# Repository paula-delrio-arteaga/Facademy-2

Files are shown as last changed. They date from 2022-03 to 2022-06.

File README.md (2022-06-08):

# Fabacademy-2
Micro challenge 2
## PHOTOBIOREACTOR

### CONCEPT

Photobioreactor hosting our algae cultures to help them grow. 

### PURPOSE

We wanted to explore the properties of algae for different individual purposes so we decided to start collaborating in the creation of the habitat for its propagation. Once we understand the species then we can be able to collaborate with them in order to develop other projects. We are interested in co-creating with algae and exploring their bioremediation abilities. After gathering enough algae we can then transform it into either food, materials, energy, biofuel, art and other individual purposes. 

### PLANNING AND EXCECUTION

We started by defining the needs of our algae and how many cultures we wanted to have. We decided to start with spirulina. We ordered the spirulina and while it arrived we started researching what we needed in order to keep it alive and help it grow. We got a manual which we are attaching in the files. From this we were able to make a list of the things we needed for cultivating the spirulina. We also reserached how the electronics would work and what parts we needed to get. After having in mind all the components neeeded then we could figure out how the design could look like. 

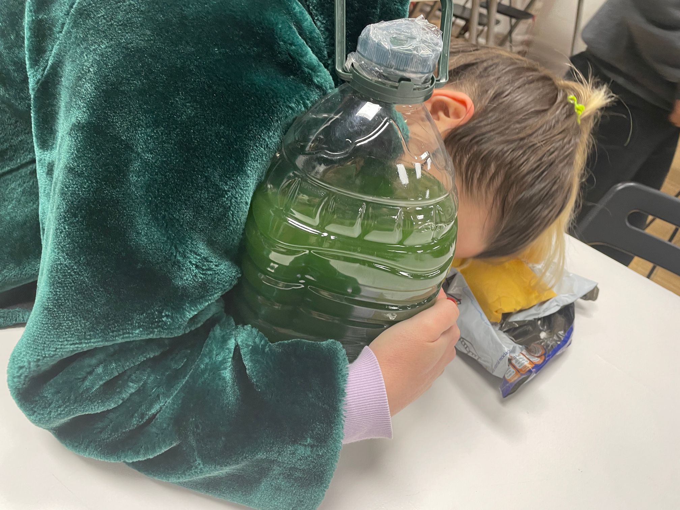
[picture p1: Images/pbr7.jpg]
spirulinalove


Now we started designing how will the spirulina be displayed and how would it work. The tricky part in this was integrating the electronics into the stand for the spirulina. Needing them to be sort of close but also protected in case of any spills.

At first we wanted to create a base box that would hold the 4 bottles of spirulina we wanted to have, one for each of us. The design was intended to have the electronics in the box with the led lights facing upwards to the spirulina. We wanted to do the box with cnc and add some curves which would be done with milling so it would add a more organic aesthethic to it. 

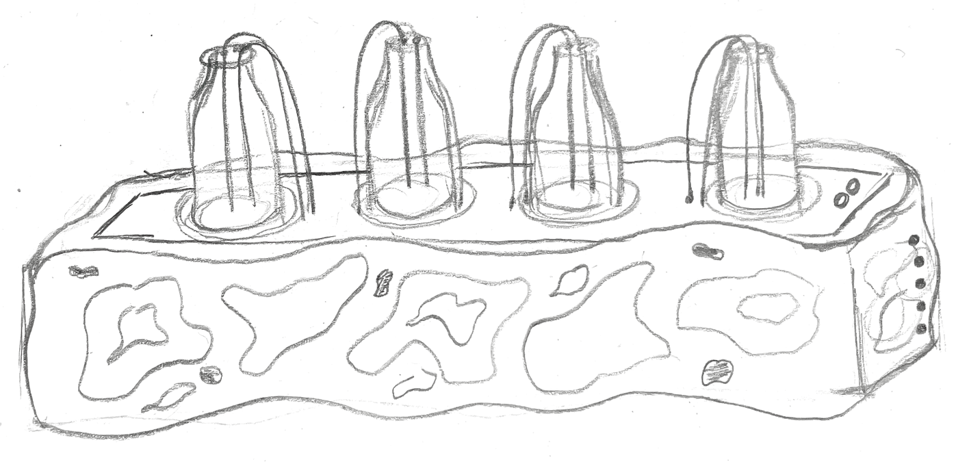
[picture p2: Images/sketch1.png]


After discussing it we realised it would take a lot of time to fabricate and we would also have a lot of kerf. After assesing this and seeing more options we decided to change the design into something that would make more sense with an organic structure around the spirulina. So we decided to test this and start sketching some ideas. When we finally agreed on a design we divided by tasks. 

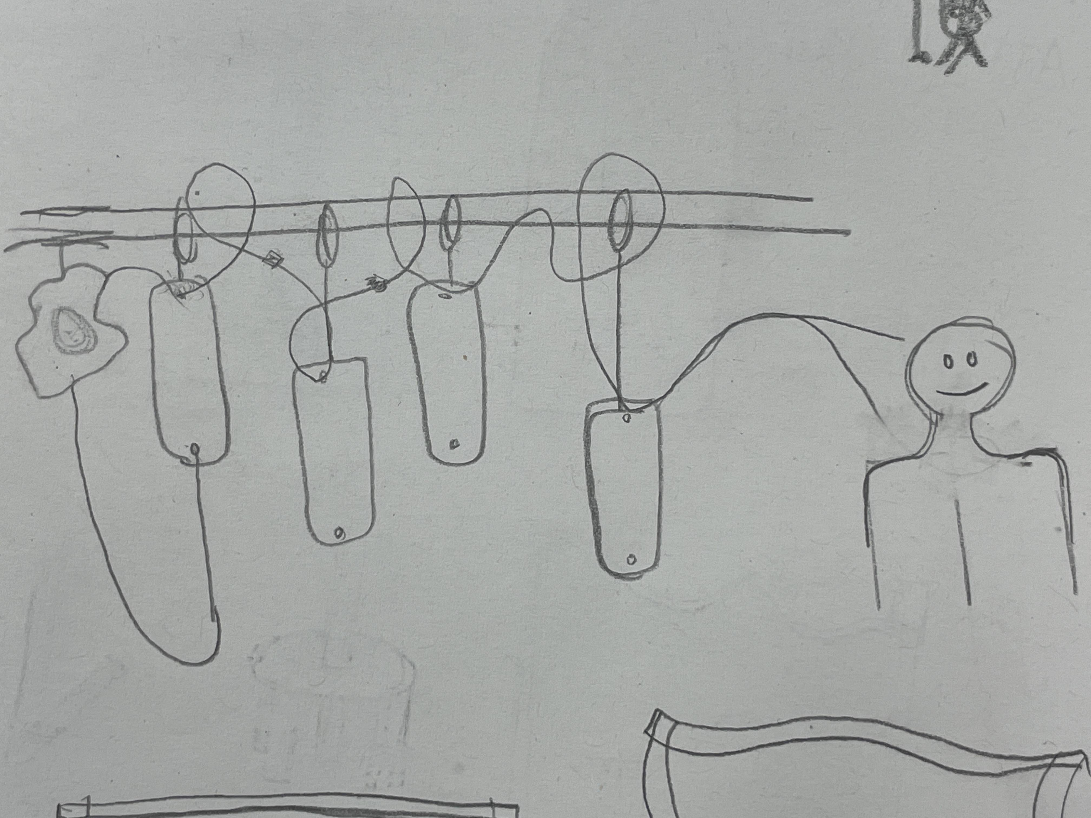
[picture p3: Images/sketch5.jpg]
sketchstand


#### CNC

  -We started making the 3D model and plans of the curves that would be fitting below the hung spirulina bottles. We 3D modelled the electronics box in which we were going to place the power, pumps, arduino and the cables. We decided to cut it in 15mm plywood. We cut 2 pieces and added a 5mm pocketing in which the LED lights would pass through, so when we glued both pieces together we could have a 1 cm rail. 
  
  -After setting up the file in rhino, we used the rhinoCam plug in and generated the code for the CNCing. We started by setting up a box which would be the material we selected and the dimensions of it. We used a board of 1200x2400x15.6 aprox. We then defined which curves would be an outer cut, inner cut and pocketing.
  
  -We also created the tool specifications, we used a Flat Mill of 6mm. We had to add the bridges in some of the pieces so they would stay in place and add the file of the screws. After defining all the settings we were ready to export the code. The screws file was exported individually and the rest of the layers were exported together. 
  
  -Once we had the nc code we went to the machine, we put out glasses, hair tie and ear cuffs on (safety first). 
  
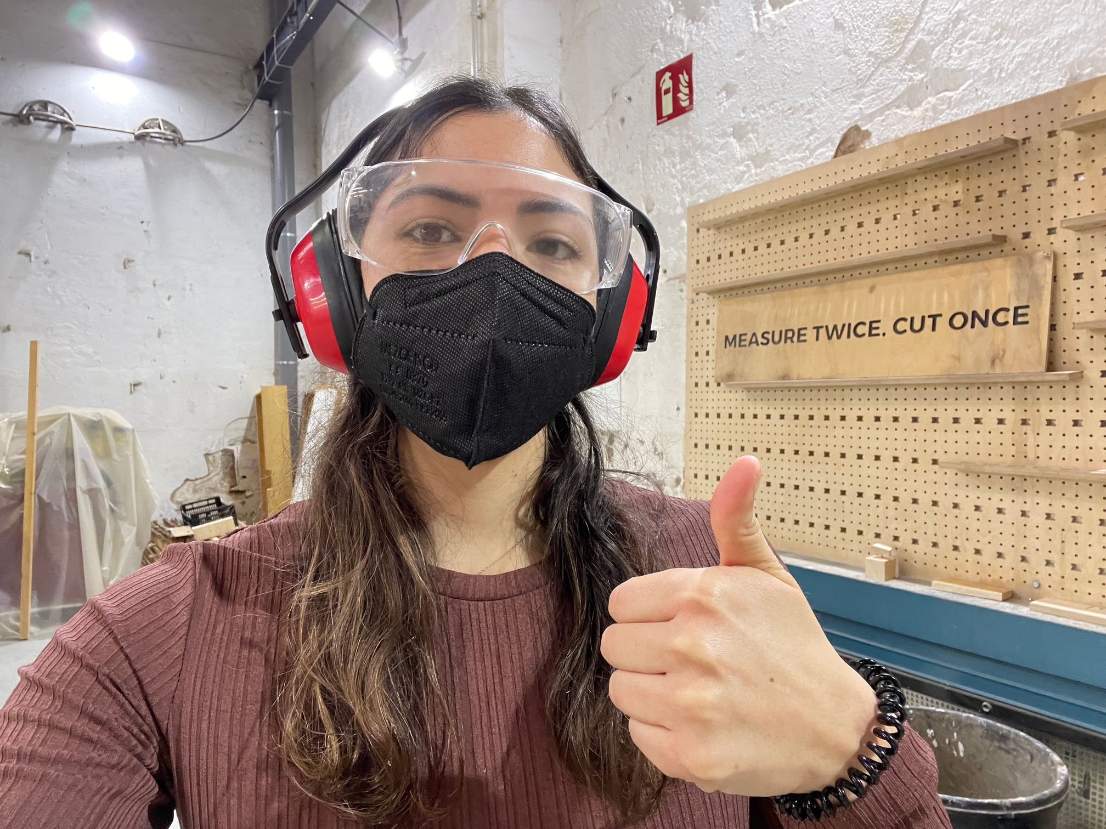
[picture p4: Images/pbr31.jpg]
safetyfirst
  
  
  -We cleaned the bed of the cnc of any extra material left from before, we placed our plywood sheet and aligned it to the borders of the bed. Then we calibrated the z axis with the button of the cnc. So we placed the button below the tip of the CNC and calibrated it. After getting that ready we opened our file in the computer and ran the screws file. 
  
  -After the marks for the screws were done we moved the head of the CNC in order to get on top and screw. 
  
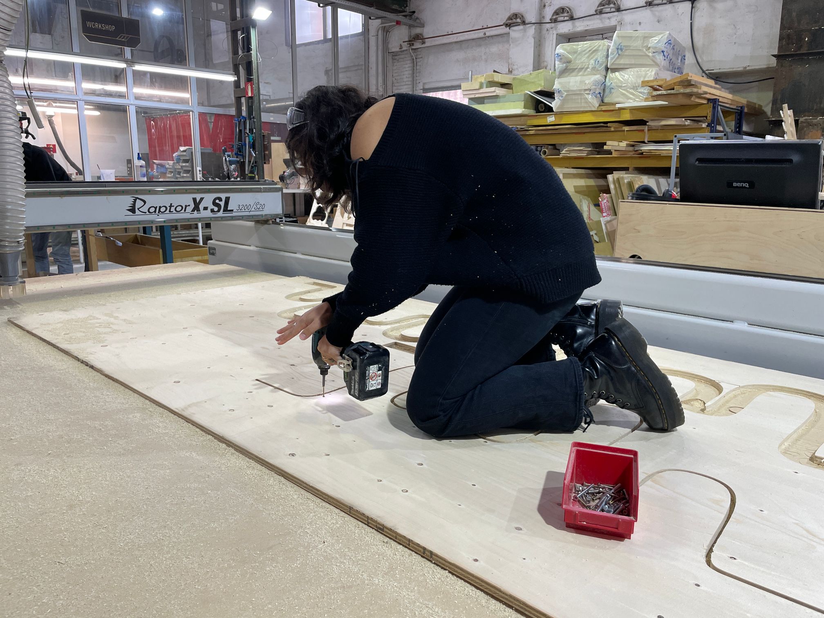
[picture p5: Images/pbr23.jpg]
screwingplywood
  
  
  -Once the material was already screwed onto the bed we were able to run the rest of the file. Our file took about 1:20.
  
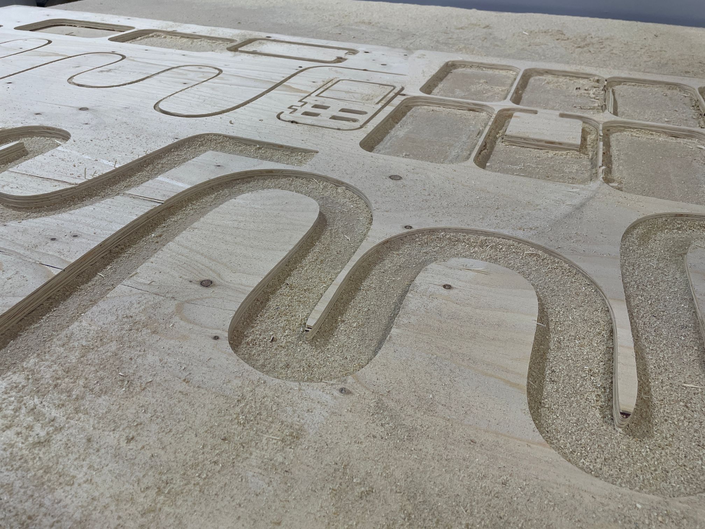
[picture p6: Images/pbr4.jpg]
cnccut
  
  
  -When the machine was done, we moved the Z axis up and moved it back so we could check if all of the cuts were done properly. After we made sure they were, we went on the bed to take out the screws and remove our pieces and the rest of the material.
  
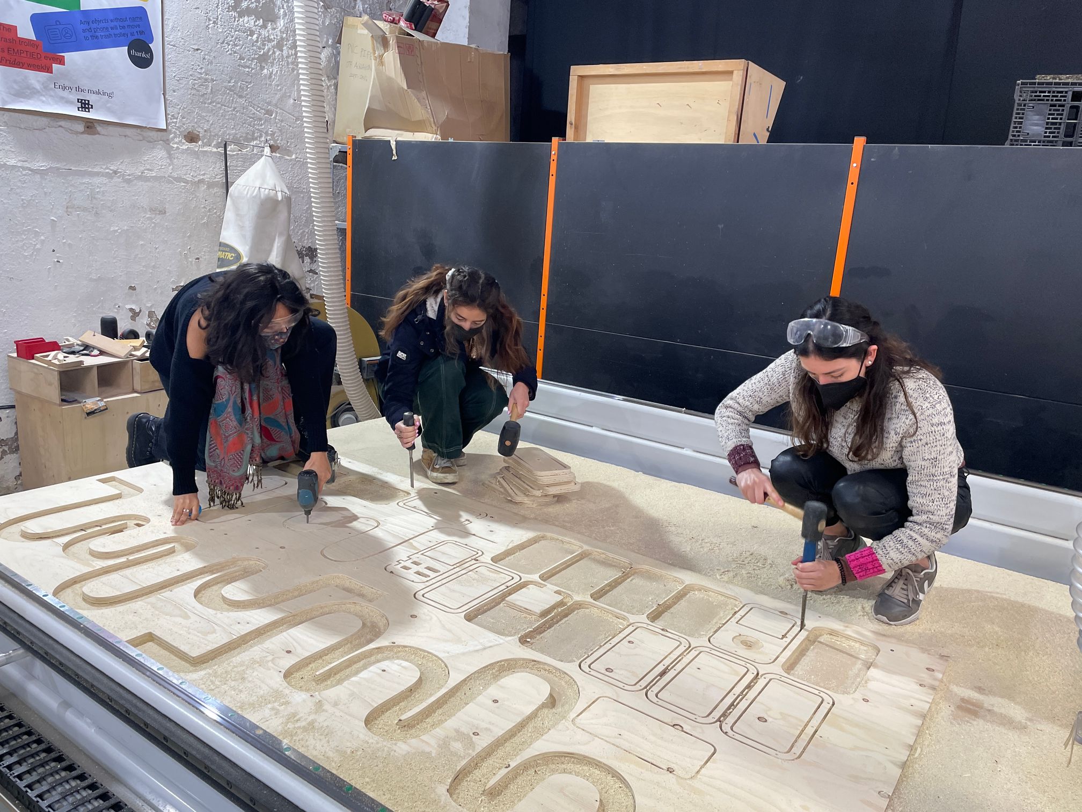
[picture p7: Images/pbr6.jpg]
bedtakingout
  
  
  -*We first had only the curves in the file and we realised we put the pocketing all the way through so we had to stop the machine and cut again but moving our pieces so it wouldn't intersect with the new cut. After cutting the curves we added the files of the box. 
  
  -Postprocessing: After getting all the pieces out, we started sanding them to remove excess bits and leave the piece smooth for assembling. 
  
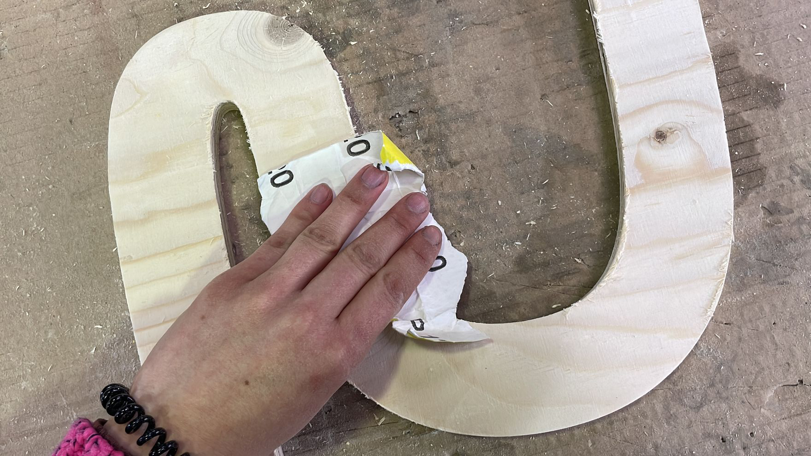
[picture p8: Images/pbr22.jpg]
sanding
  
  
  -Once the curves were ready we were able to glue them together. We applied a thin layer of glue and then used the clamps to hold it together while the glue was doing its job.
  
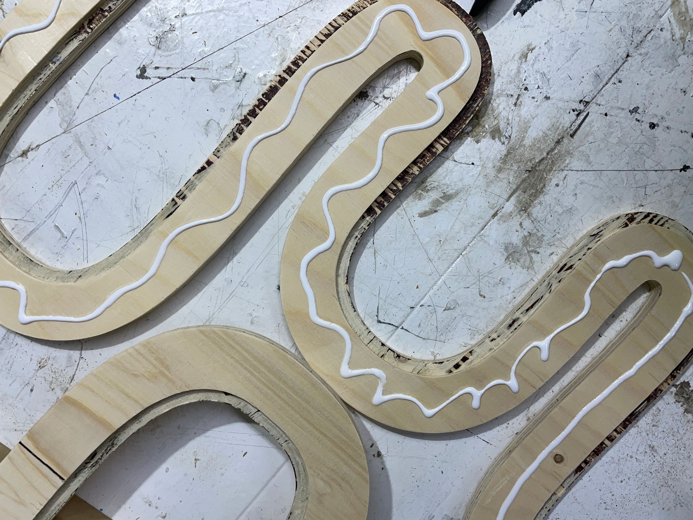
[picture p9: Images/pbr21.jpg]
curveglue
  
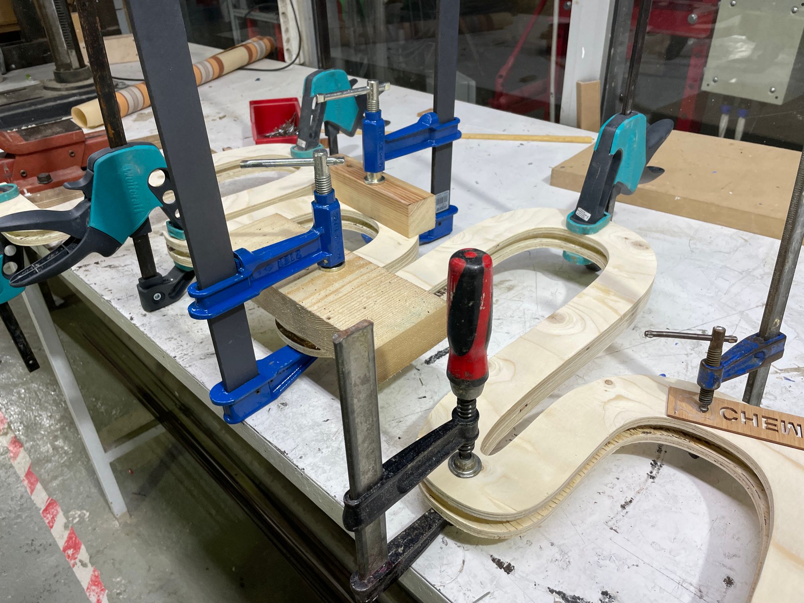
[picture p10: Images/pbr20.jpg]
curveclamping
  
  
#### 3D PRINTING

  -We prepared the 3D files for 3D printing. 
  
  -Understanding first the pieces needed and their functions. When the type of joineries were defined we started measuring the dimensions of the material they would be attached to in order for them to fit correctly.
  
 -After making the 3D model we went to the machines to start setting up the file in CURA and PRUSA in order to send them to the machines. We used PLA in white and black for different pieces. We did some tests before and then we were ready to start 3D printing. The parameters we had were 210 heat of the nozzle and 60 heat of the bed. The longest print took 14 hours. 
 
 -We ran five machines at the same time in order to make better use of our time. 
 
 -When the printing was done we had a bit of a struggle to take out the material because it got stuck to the bed. We used the spatula to scrap them off and after some struggle they came out. 
 
 -We spent some time taking out the extra filaments for support and sanding a bit some parts. Then we were able to assemble them for the stand. 
 
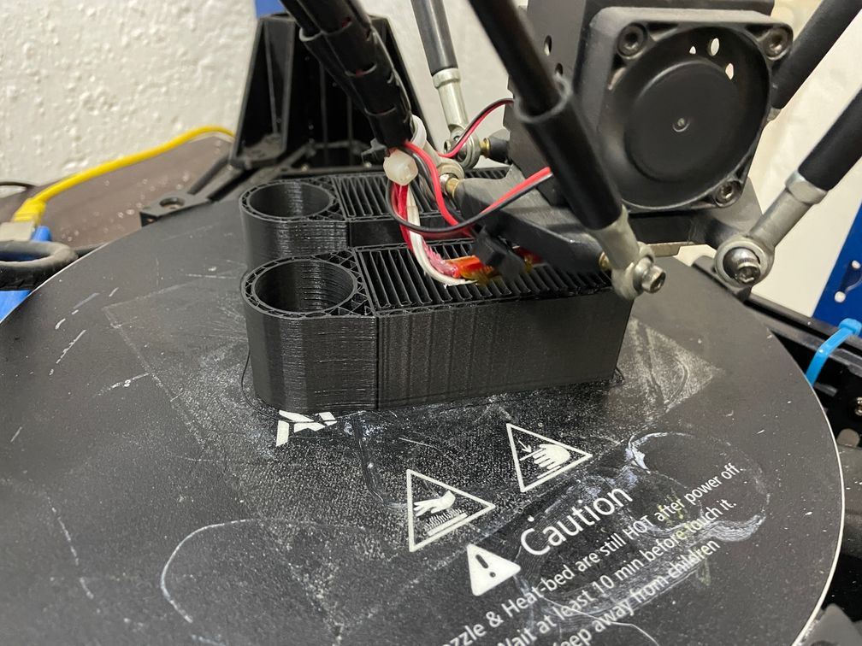
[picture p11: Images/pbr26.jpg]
3dprinting1
 
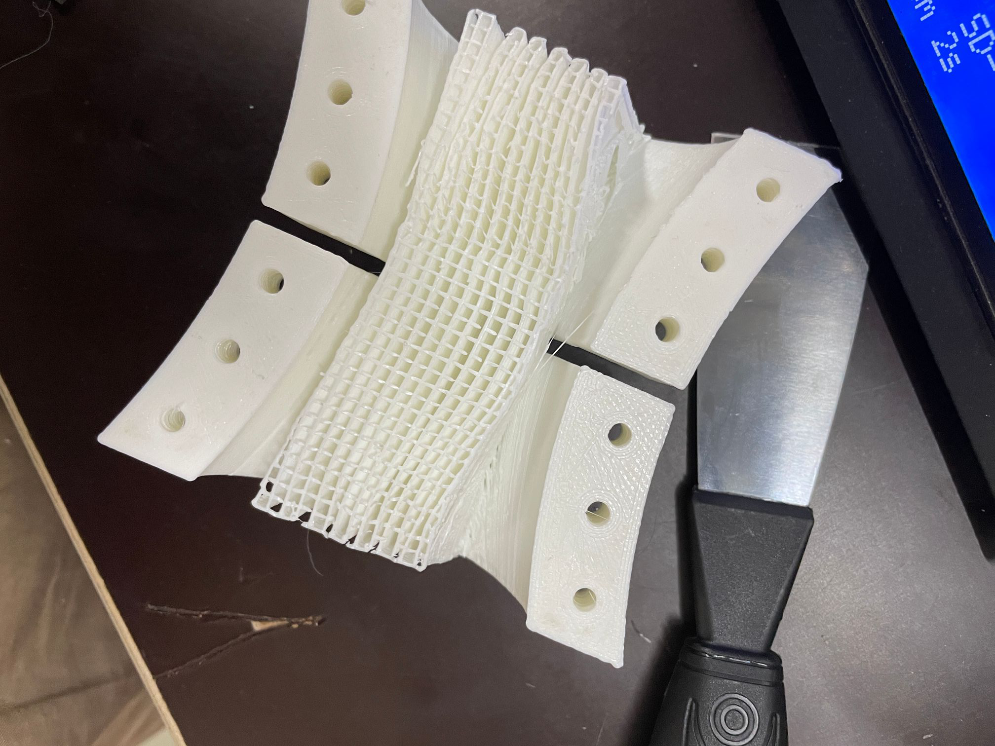
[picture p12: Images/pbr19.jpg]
3dprinting2
 
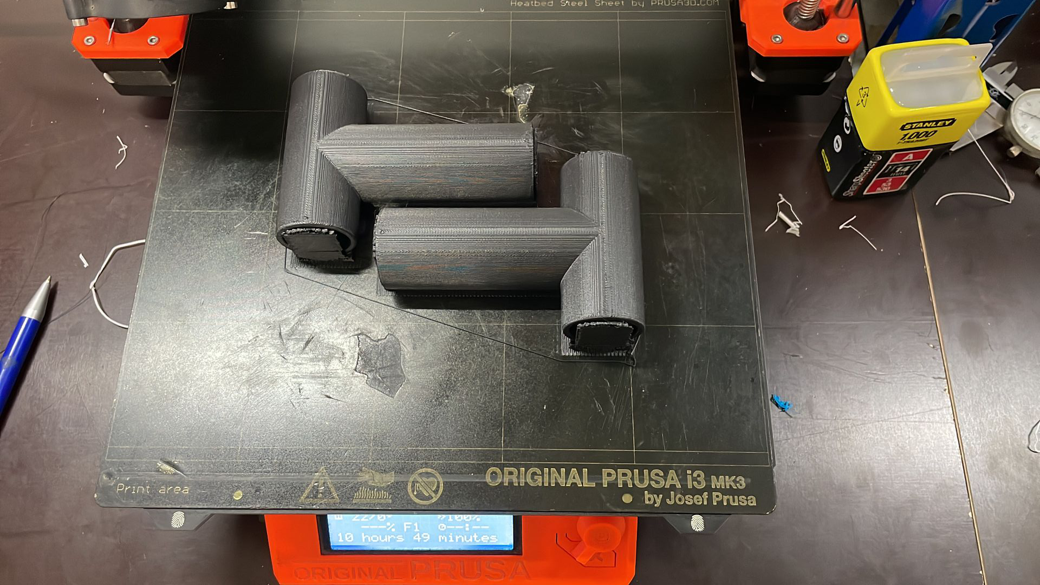
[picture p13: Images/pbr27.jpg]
3dprinting3
 
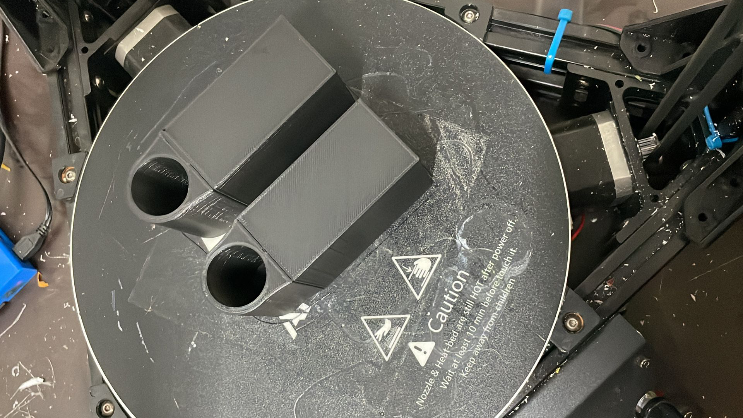
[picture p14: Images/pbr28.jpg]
3dprinting4
 
 
 #### ELECTRONICS
 
  - Figuring out all the connections to the power supply since we have an Air Pump of 220v, a peristaltic Pump of of 12v and a LED strip of 12v plus our microcontroller ESP32 feather to controll the timing of each component. 
  - We thought we could use the power supply (12v 1A) from the LEDs to also connect the peristaltic pump since it has the same voltage. But after checking how many ampers each component needs, we decided to swith all the connections to a bigger power supply of 12v with 16.5 Ampers. In case we need to scale the project we would be able to connect more pumps to the same power supply. The LED requieres a 0.85 Ampers and the peristaltic pump 0.2 Ampers. 
  
  - When all the connections and wiring was done we work on configuring the code. The code consisted on a set of different functions that controlled the 2 pumps indpendantly an the leds. The Air pumpwas controlled by the relay and the other componentes by 2 mosfets. 
  
  - When a certain amount of milliseconds has passed we enter the void to start the pump and we keep counting if the time is more or equal to the starting time we leaeve the pump on and after if the time is more or equal to the other variable, that determines the amount of time the pump has to be on, we turn the pump off.
  
  - We also added a funcition to dim the leds.
 
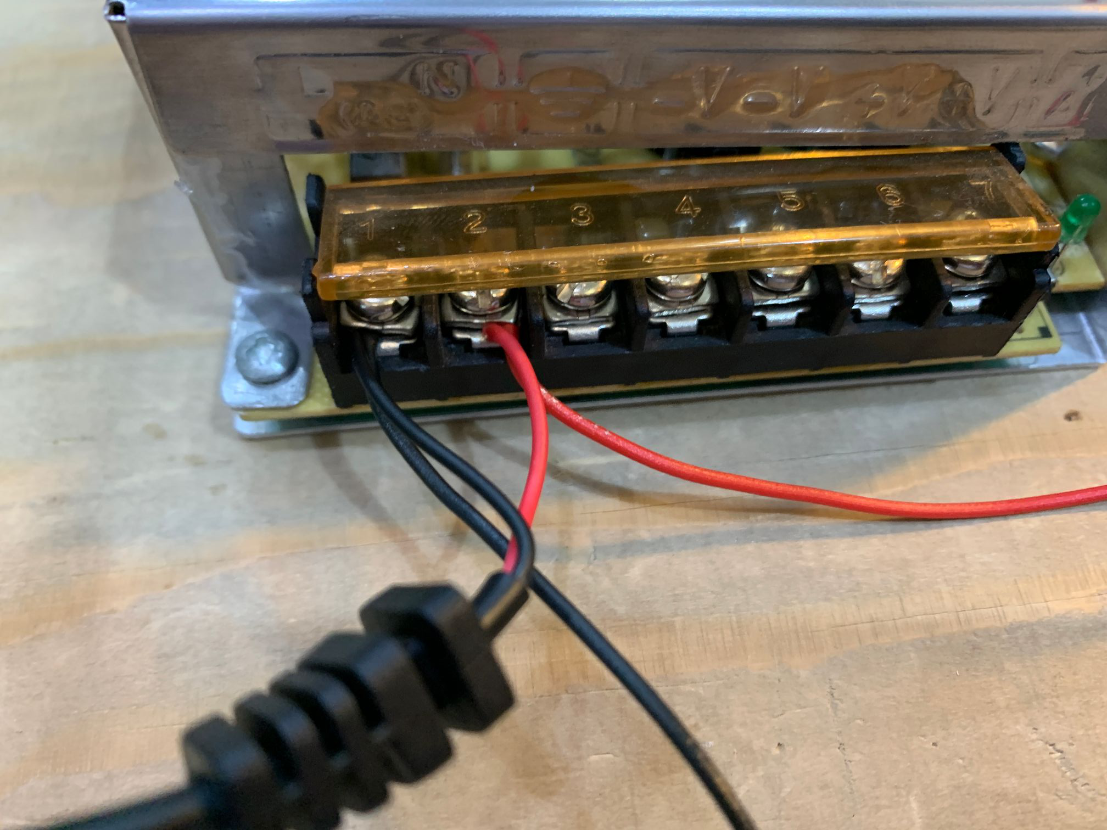
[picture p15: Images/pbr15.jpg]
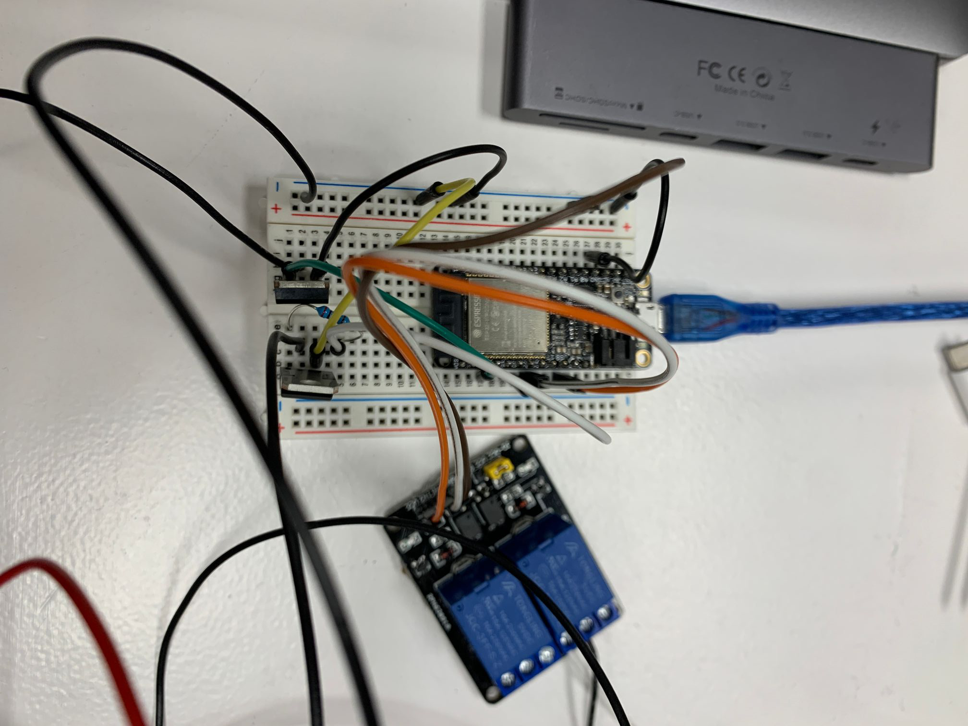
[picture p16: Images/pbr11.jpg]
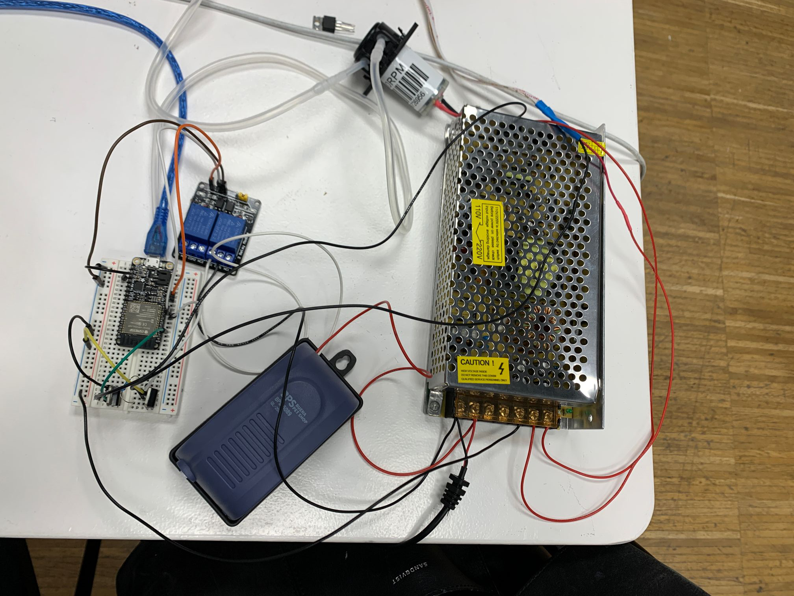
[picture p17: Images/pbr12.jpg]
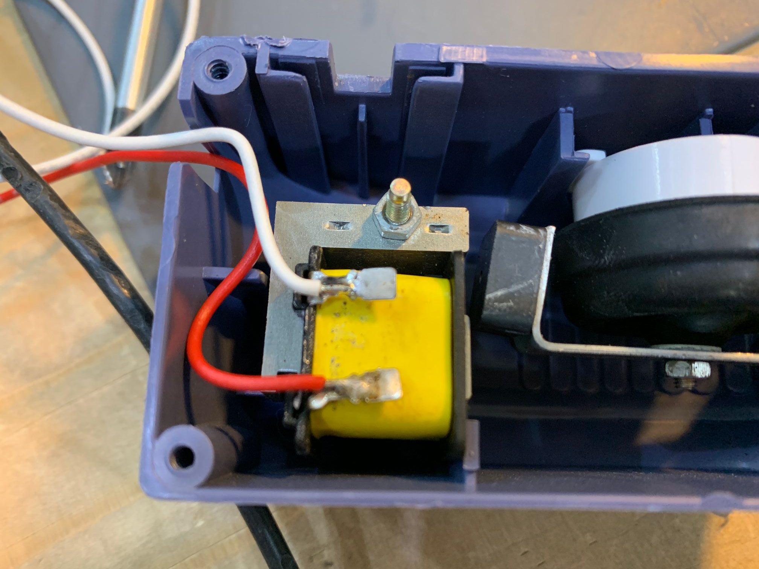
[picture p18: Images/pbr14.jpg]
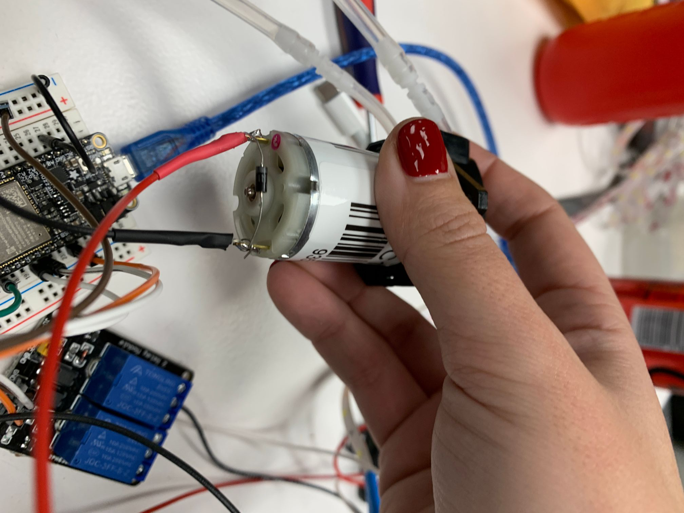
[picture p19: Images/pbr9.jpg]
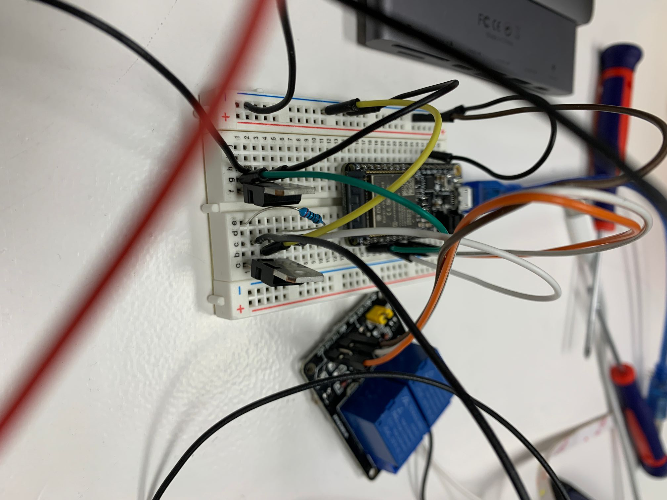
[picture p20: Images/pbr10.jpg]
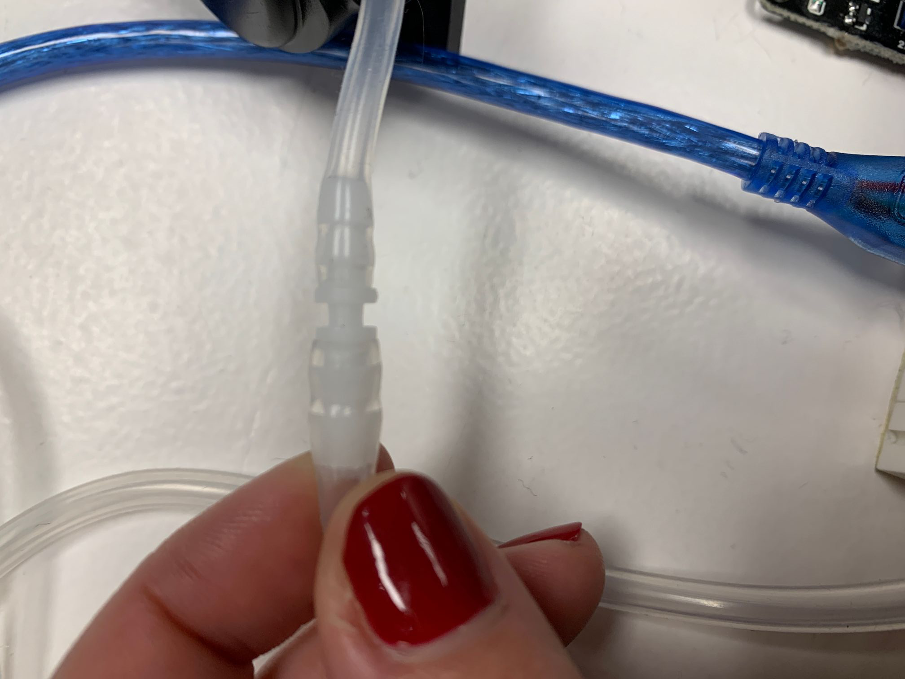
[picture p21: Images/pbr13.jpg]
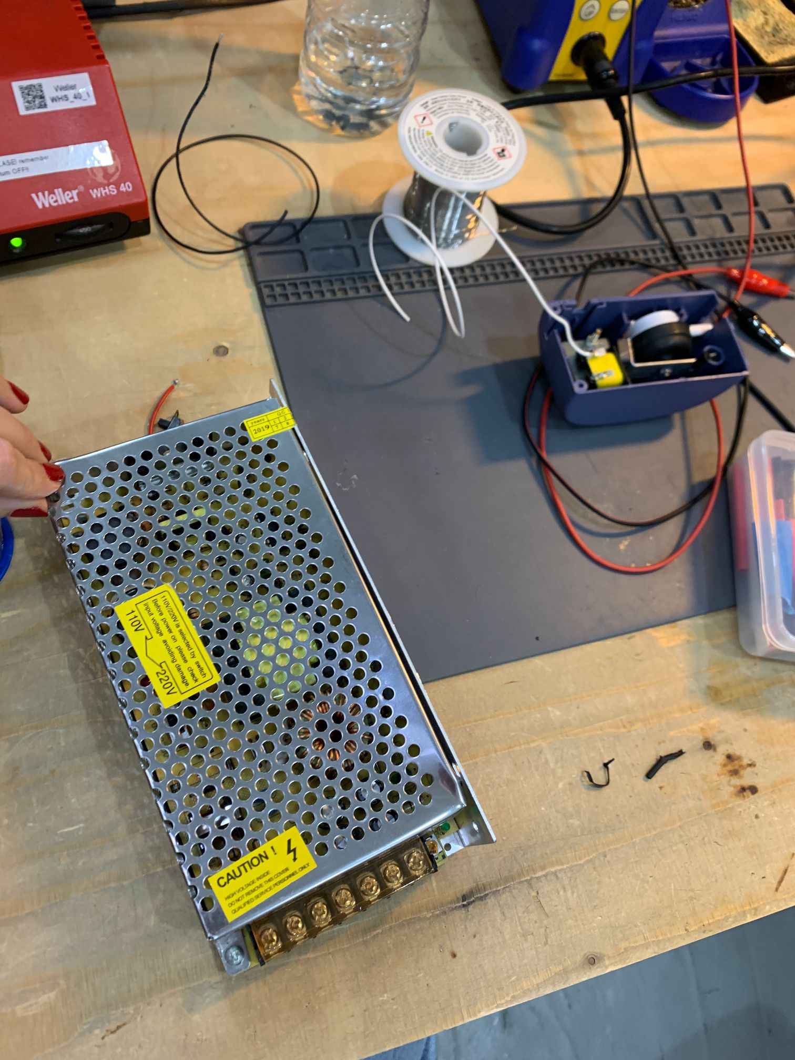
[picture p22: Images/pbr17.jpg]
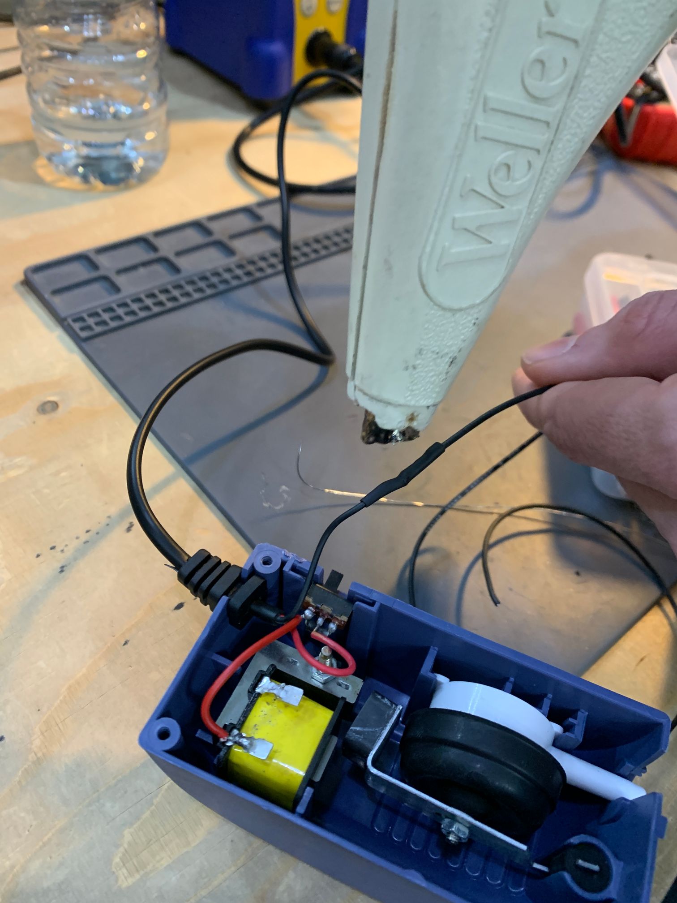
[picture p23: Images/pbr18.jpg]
        
 
 #### LASER CUTTING
 
  -We decided to laser cut an acrylic lid for the electronic box the have electronics visible. 
  
  -We prepared the file in rhino and inserted the GROW LAB text for it to be engraved. Once it was done we opened the file in the computer, calibrated the laser cutter with the tool. Chose our material and moved the laser to where we wanted it to start cutting. After this then we put the parameters for acrylic and the type of cut and we sent the job. 
  
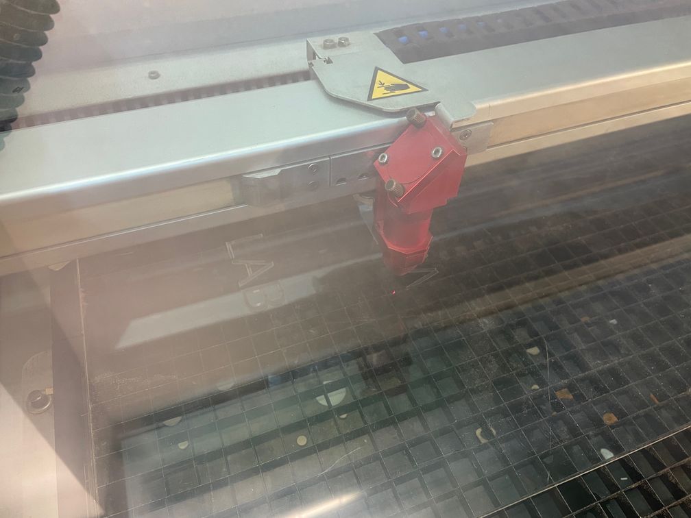
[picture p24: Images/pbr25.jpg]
acryliccut
 
 
 #### 3D SCANNING
 
  -We wanted to test the 3D scanning tools so we chose to use it to 3D model the neck of the bottles we would use in order to fix them to the rail. 
  
  -As the bottle is clear we then had to tape it around so the phone was able to identify the volume and scan it. 
  
  -This was a bit complicated and in the end the redult was not desirable and we went back to just measuring the different diameters in the bottle neck. 
  
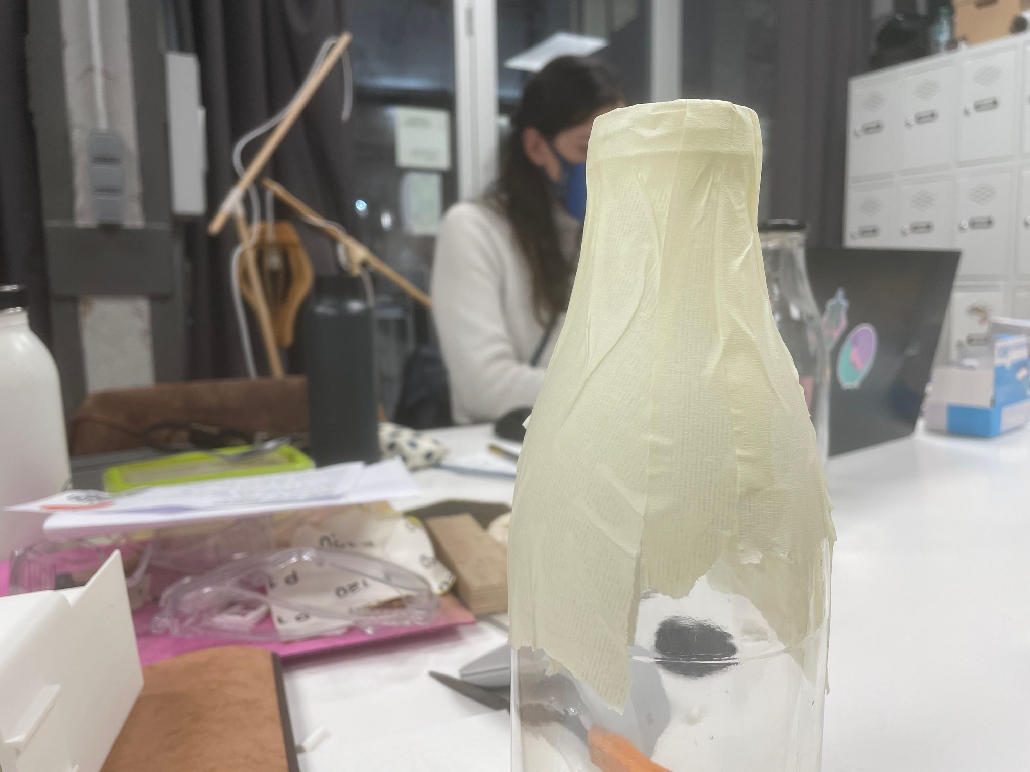
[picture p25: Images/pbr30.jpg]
3dscanbottle
  
  
 #### ASSEMBLING
 
  -After having all our pieces together it was time to assemble them together. We started by trying to fit them and making adjustments like sanding or drilling in case they didn't fit perfectly and then put everything we had into place. 
  
  -Making the stand, we measured the dimensions we wanted the stand to have and then sanded the rod so it could fit well into the 3D pieces. 
  
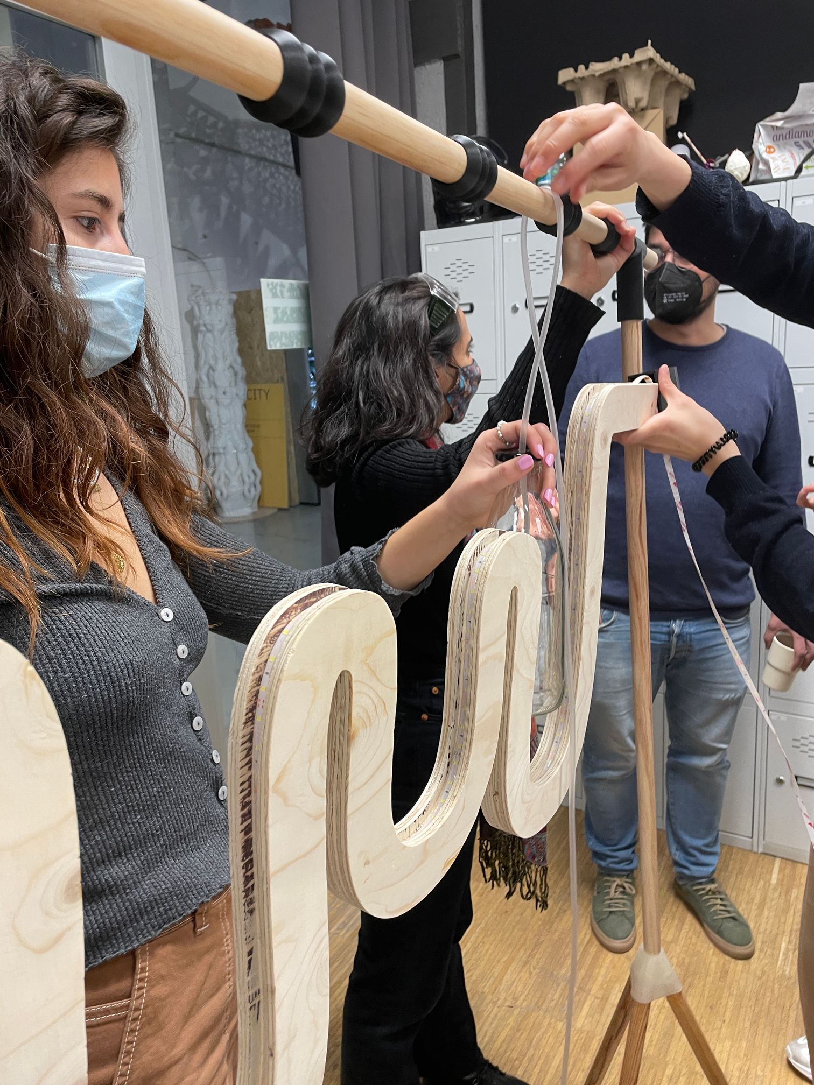
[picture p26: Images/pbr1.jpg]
assemblingrack
  
  
  -We also had to figure out how would the tubing system would work and where they would go into the bottles and out from them. We drilled holes into the top of the bottle caps so the tubes would come in and out.
  
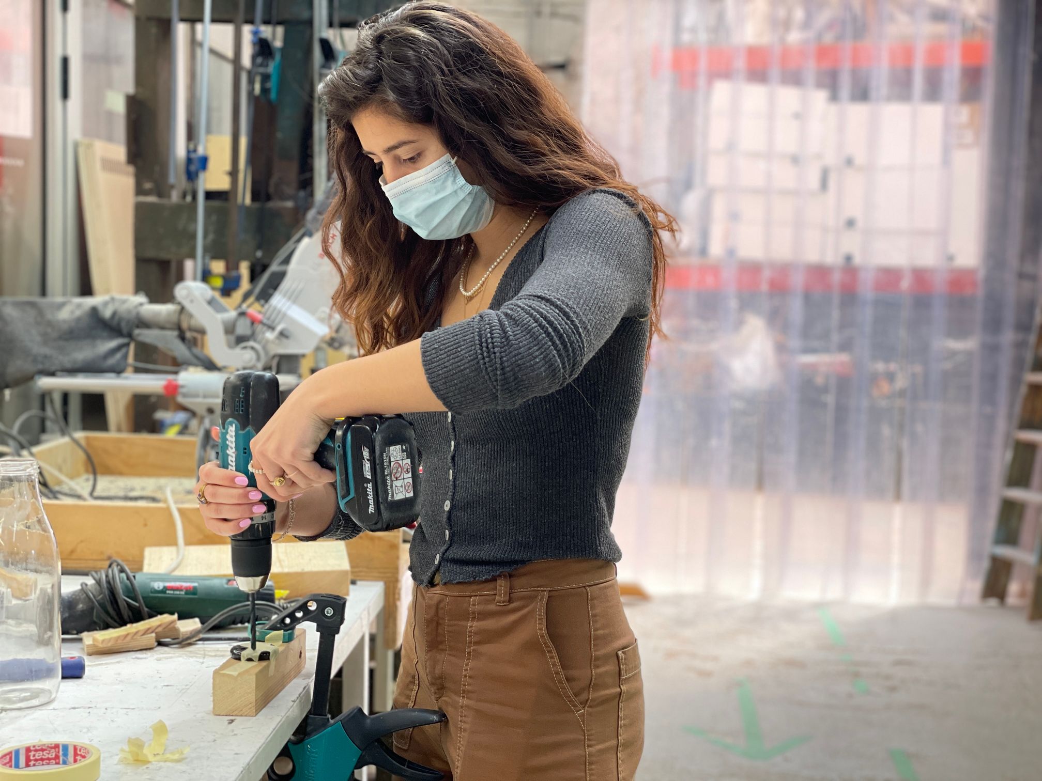
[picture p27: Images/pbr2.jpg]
marinadrill
  

### SYSTEM DIAGRAM (FUNCTION, PARTS, RELATIONS)

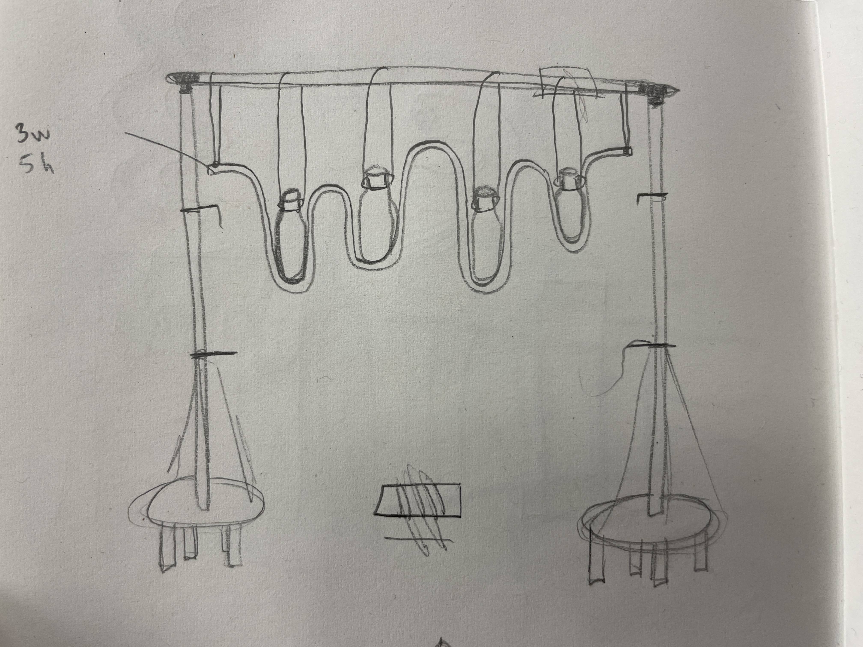
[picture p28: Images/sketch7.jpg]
hangingbottlestand


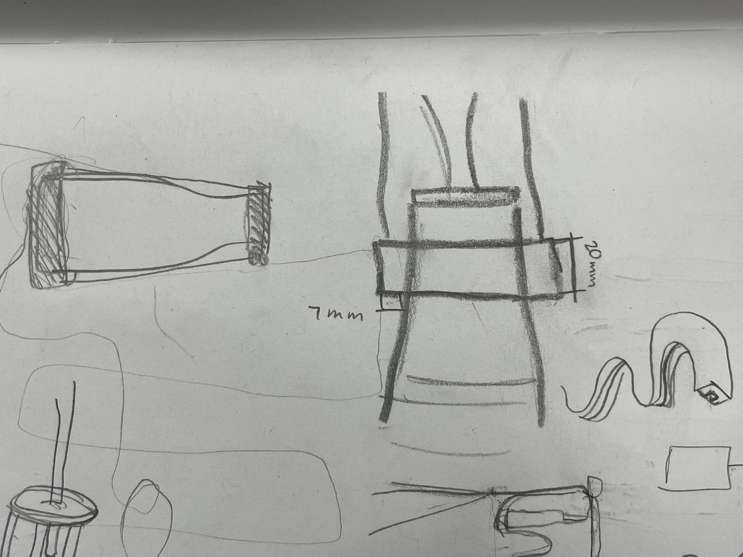
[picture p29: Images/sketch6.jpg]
bottlehugger


### DESIGN ELEMENTS (HOW YOU DESIGNED IT)

### DESIGN AND FABRICATION FILES

  #####ELECTRONICS BOX
  
  assemblingrack
  
  #####CURVES
  
  assemblingrack

  #####CODE
  
  assemblingrack
  
  ####3D PRINTING FILES
  
  assemblingrack
  
  assemblingrack
  
  assemblingrack

### BOM (BUILD OF MATERIALS) 

### CODING LOGIC (ALGORITHMS AND FLOWCHARTS, PSEUDOCODING)

### FINAL PRODUCT

## NOT READY!

### ITERATION PROCESS

- We struggled first to find a design that could fit our necessities, the algae's and the electronic's. In this case we prioritised figuring out the electronics first and then seeing how we would connect them to the design.

-Our idea at some point was to CNC the stand but when testing the resistance of the material we realised it wasn't going to hold the weight of our bottles. Also if we CNC'd the stand it would have been a lot of material and a lot of waste. We decided to simplify the stand and use pine wood rods attached to joints that would be 3D printed. 

-One 3D printed piece broke when we were trying to take it out of the bed so we had to 3D print a new one which set us back a bit. But we managed to move on with another task in order to make the most of the time we had left. 

-While assembling our stand one of the 3D printed joints that was holding our curve broke so we had to tape it in the meantime while we printed a new one.

-We had some difficulties understanding the logics of the pump and the tubing system. So we spent a lot of time trying to make sense of it and testing it. 

-All of this while also taking care of our spirulina which had us a bit nervous it would be dying but with the pumping system and the microcontroller turning it on every 25 min for 5 min, we had it all under control.

### FUTURE DEVELOPMENT OPPORTUNITIES

-For our future development plans we want to continue improving the design until we find something that fits our purposes. We all have different ideas for this spirulina growing system we would like to develop further. We would like to explore the possibility of making it more compact and portable. Now that we know the logics of it we could figure out a way to compact everything into a smaller design. For now we are only focusing on the growth of the algae but in the future we would like to add other sensors that could track down the amount of CO2 it is sequestering or transforming this system into a biophotovoltaic system generating energy, exploring what we could do with the spirulina like using it as food, biomaterials or even biofuel. 

### LINKS TO INDIVIDUAL PAGES

https://paula-bustos.github.io/peebee/

https://marina-lermant.github.io/mdef-website/

https://philippa-formosa.github.io/mdefweb/

https://paula-delrio-arteaga.github.io/mdef/

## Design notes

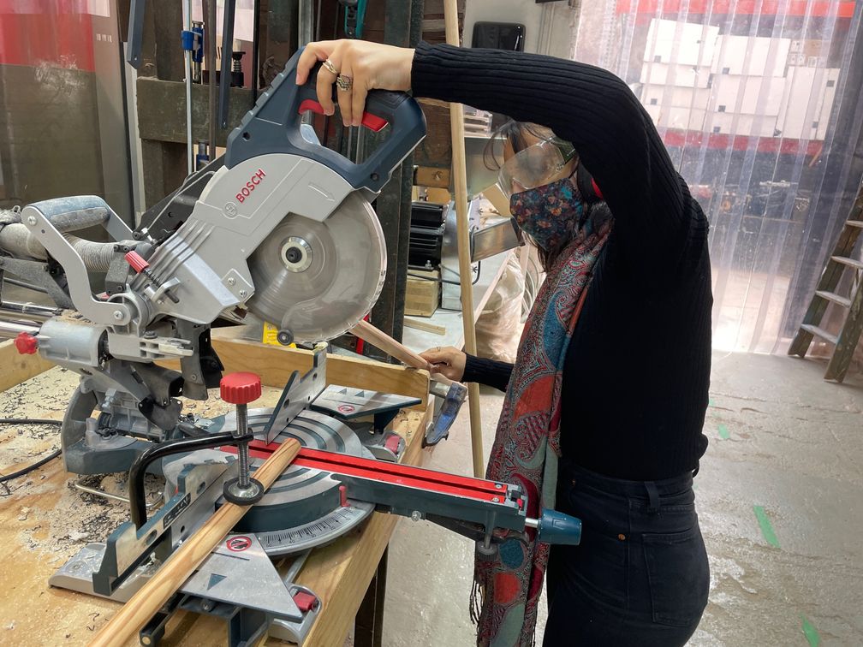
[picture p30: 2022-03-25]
Images/pbr24.jpg

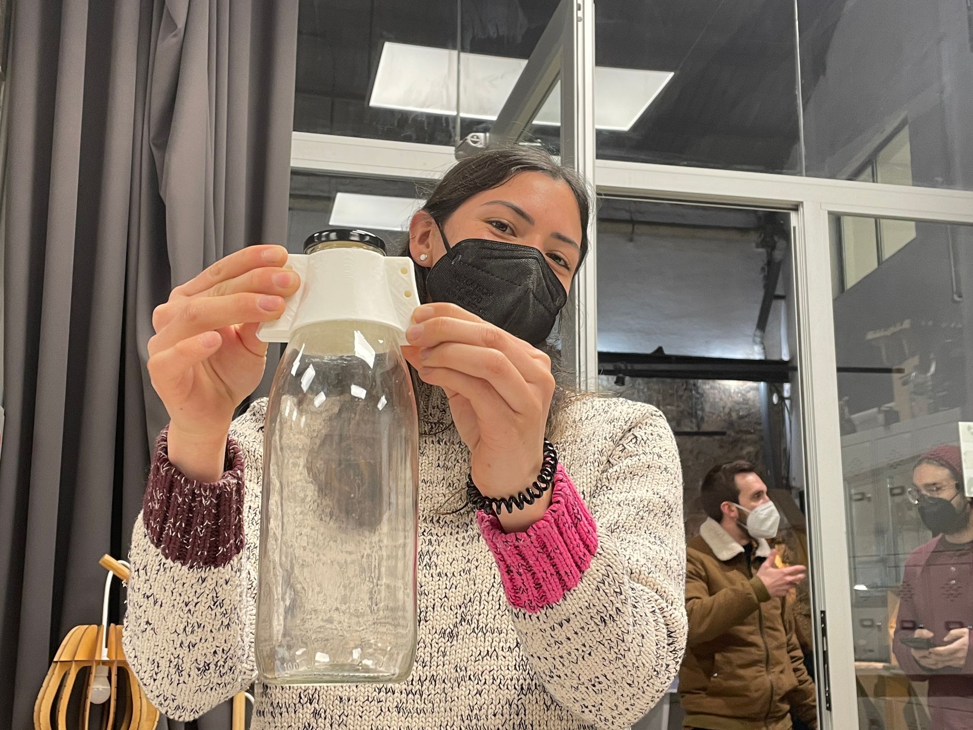
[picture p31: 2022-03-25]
Images/pbr3.jpg

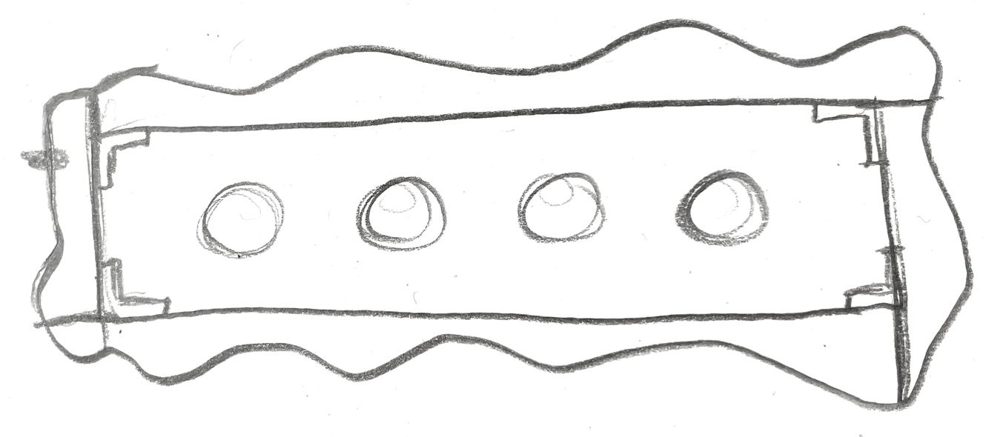
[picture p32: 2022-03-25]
Images/sketch3.png

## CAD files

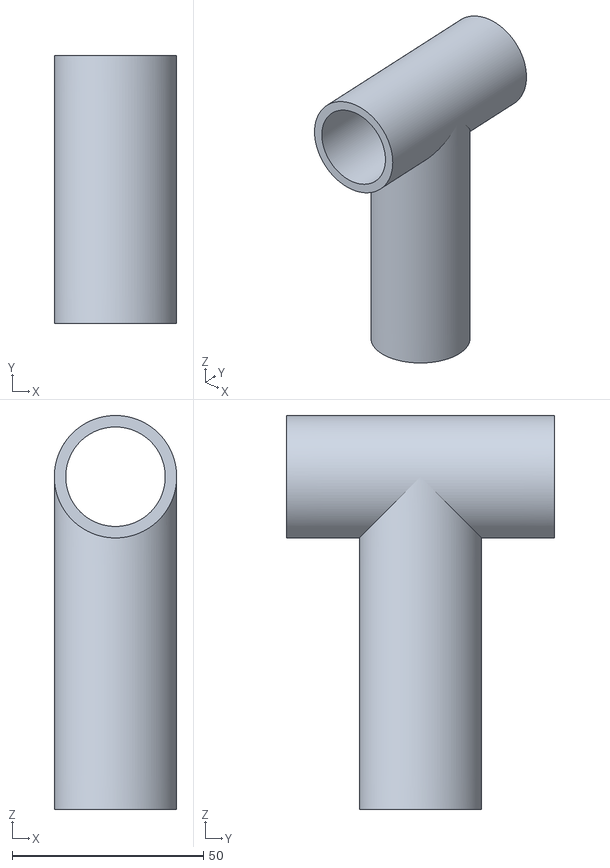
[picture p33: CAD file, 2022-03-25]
Files/joint 2.stl
32.0 x 70.0 x 103.0

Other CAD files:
Files/Box Cutting file.3dm
Files/curvesbottles.3dm

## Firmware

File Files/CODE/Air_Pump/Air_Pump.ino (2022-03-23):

//1.1///////////////// Init Pump Timer ///////////////////

// Pump Test
//const long pumpInterval = 10000;
//const long pumpRuntime = 2000;

//Pump spirulina
const long pumpInterval = 3600000;
const long pumpRuntime = 300000;

unsigned long lastTimePumpStart = 0;

int Relay = 13;

int statusIndicatorLED = 27; // Status LED


void setup() {

  pinMode(Relay,OUTPUT); // Set Relay Output
 
  pinMode(statusIndicatorLED,OUTPUT); // Set Indicator LED Output

  ///////////////////
  
  Serial.begin(115200);
  Serial.println("Setup finished");
}


void loop() {

//Pump Control
  if (millis() - lastTimePumpStart >= pumpInterval) {
    lastTimePumpStart = millis();
    digitalWrite(Relay,HIGH);
    digitalWrite(statusIndicatorLED, HIGH); // Indicating Pump Start
  }

  if (millis() - lastTimePumpStart >= pumpRuntime) {
   digitalWrite(Relay,LOW);
   digitalWrite(statusIndicatorLED, LOW); // Indicating Pump Finish
  }

}
